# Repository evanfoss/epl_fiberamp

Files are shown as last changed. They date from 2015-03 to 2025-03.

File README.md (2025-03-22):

# EPL FiberAmp

## Description

This device was used with an optical sensor to measure sound pressure levels in space constrained environments. The That end was the sensor the other end of the fiberoptic line was attached to a splitter connecting to two more lines that went to the output and input of this device. The FiberAmp supplies a low noise light source to illuminate down the fiber and a photodiode with matching high gain transimpedance amplifier with AC and DC coupled outputs. The AC coupled output was for making measurements of the sound. The DC output was used for verifying the delicate gold coating was not damaged and that light is still reflecting off of it.

Note: Those of you more aware of physics might want to skip to the section at the end titled "Future".

## Development

Most frequently along the auditory path of cadaver ears. The sensor was a fiberoptic line with a thin gold coating deposited onto it's end viaan evaporation process. The original concept was proved by Lisa Olsen's team earlier. The electronics for this were however started with a clean sheet by Evan Foss and the DC filter network from the earlier EPL revision by Ishmael S. W. The reasoning was simple, the original design and a revised update from EPL earlier were very old and both had seen numerous itterations that added amplifier stages haphazardly. There was also the issue of stability. The earlier EPL update was about 15 years old at least and it was known for periodically becoming unstable and self oscillating for unknown reasons.

### Alternate Versions and Experiments

Part way into the process the project was canceled, later it was uncanceled. This happened a few times. Along the way other features were requested and canceled.

|Feature or Concept         | Designed                  | Tested                | Observations
|:---------------           |:---------------           |:---------------       |:---------------
|Infrasound Measurement     | Yes                       | No                    | The 1/f noise etc of the amplifiers made this notion crazy once more there was serious doubt from the team making the sensors that they were responding at that scale
|Reverse Bias on photodiode | Yes                       | Yes                   | This had no obvious effect on THD+N and was abandoned
|Alternatives for 1st stage opamp| Yes                  | No                    | I had drawn up early versions with a few alternative opamps for that first stage because it was unclear on paper which would perform better

## Toolchain

The development toolchain was as follows:

|Tool Name                                                                                   | License           | Function
|:---------------                                                                            | :-------------    | :-----------------
|<a href="https://www.sagemath.org//">SageMath</a>                                           | Open Source       | Online Mathematics Software
|<a href="https://github.com/lepton-eda/lepton-eda">lepton-eda</a>                           | Open Source       | EDA (Electronic Design Automation) suite lepton-eda a fork of gEDA
|<a href="https://ngspice.sourceforge.io/">ng-spice</a>                                      | Open Source       | Circuit Simulator
|<a href="http://repo.hu/projects/pcb-rnd/">pcb-rnd</a>                                      | Open Source       | CAD (Computer Aided Design) tool for PCB (Printed Circuit Board) layout gEDA/PCB
|<a href="https://gerbv.github.io/">gerbv</a>                                                | Open Source       | Gerber viewer
|<a href="https://www.gnu.org/software/make/">GNU/Make</a>                                   | Open Source       | Toolchain automation
|<a href="https://www.frontpanelexpress.com/front-panel-designer">Front Panel Designer</a>   | Free as in Beer   | Front Panels Express Software

Sadly all my SageMath entries for this project appear lost. I believe a SageMath server refresh some years ago took them out.

The PCB layout was originally done in gEDA/PCB which I believe is defunct. Thankfully pcb-rnd which forked from that project is still fully backward compatible to it.

A partial simulation of the device was created to see how the integrators would behave. It is in the "simulation" directory. I had intended I think to add more to simulate the reverse bias and other ideas but there is so much about the sensor that would need to be characterized for that. All that measurement would basically be just as time consuming and expensive as building a few versions and testing them which was contentious with this projects PI.

## Circuit Design

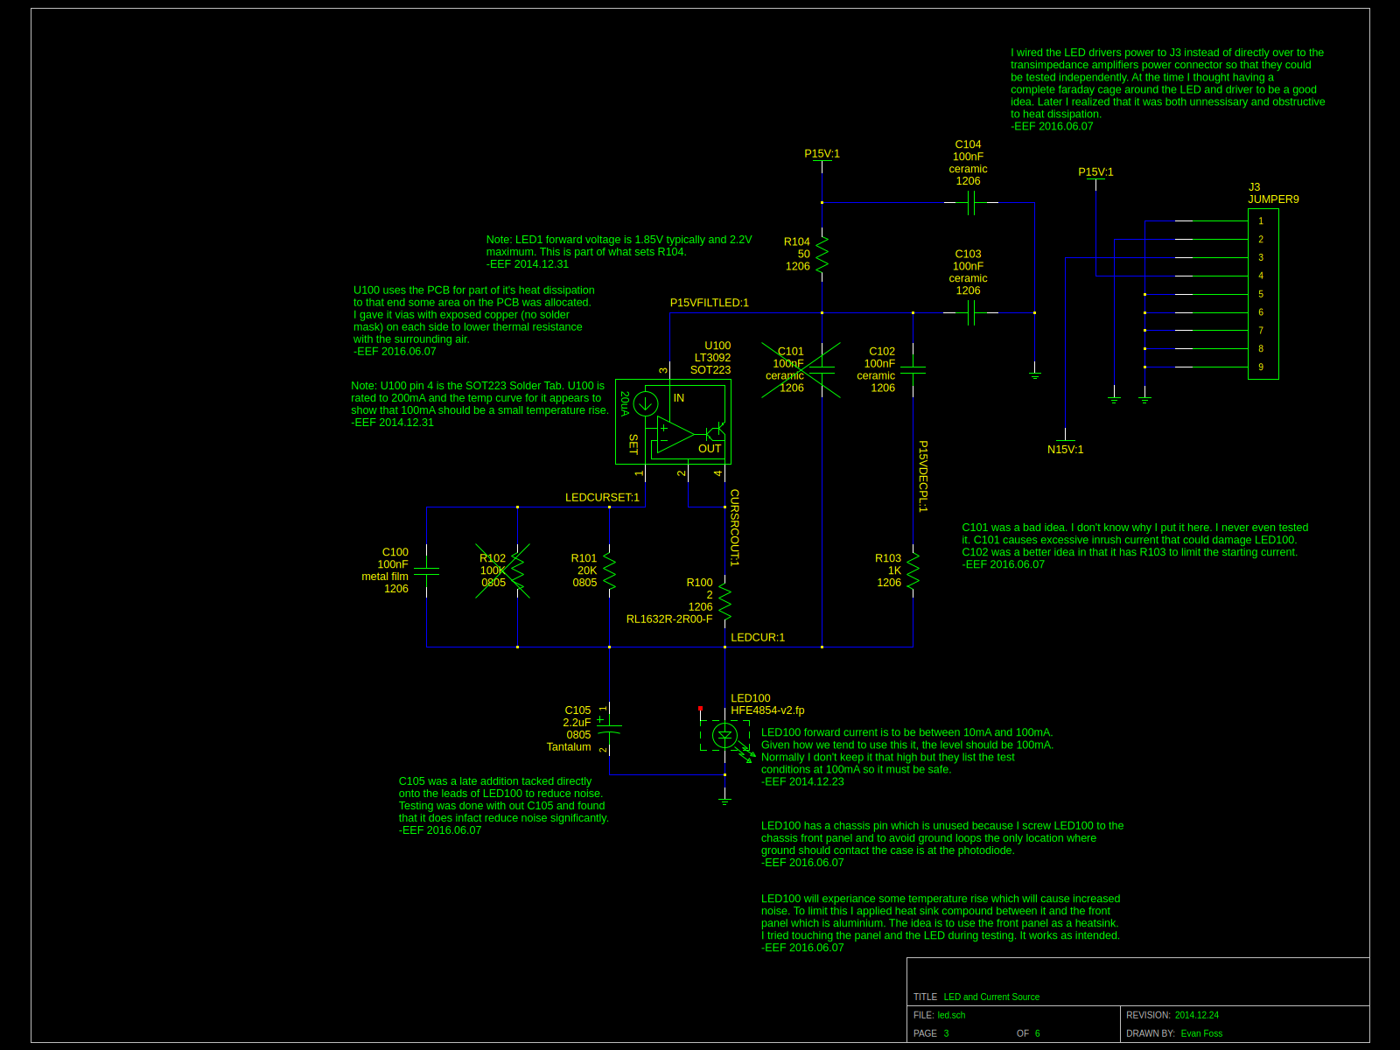
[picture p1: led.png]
|
|:-----------------
|Sch1: led.sch

Sch1 shows the light source for the project. LED100 is the lightsource. The U100 is a constant current source. R104 and C103 attenuate ripples in the power supply and it lowers the amount of power dissipated in U100 and it limits the initial current through C105. R100 is a current shunt. R101 sets the current and C100 reduces the noise R101 contributes. Likewise C105 reduces noise and limits power on current through LED100. 

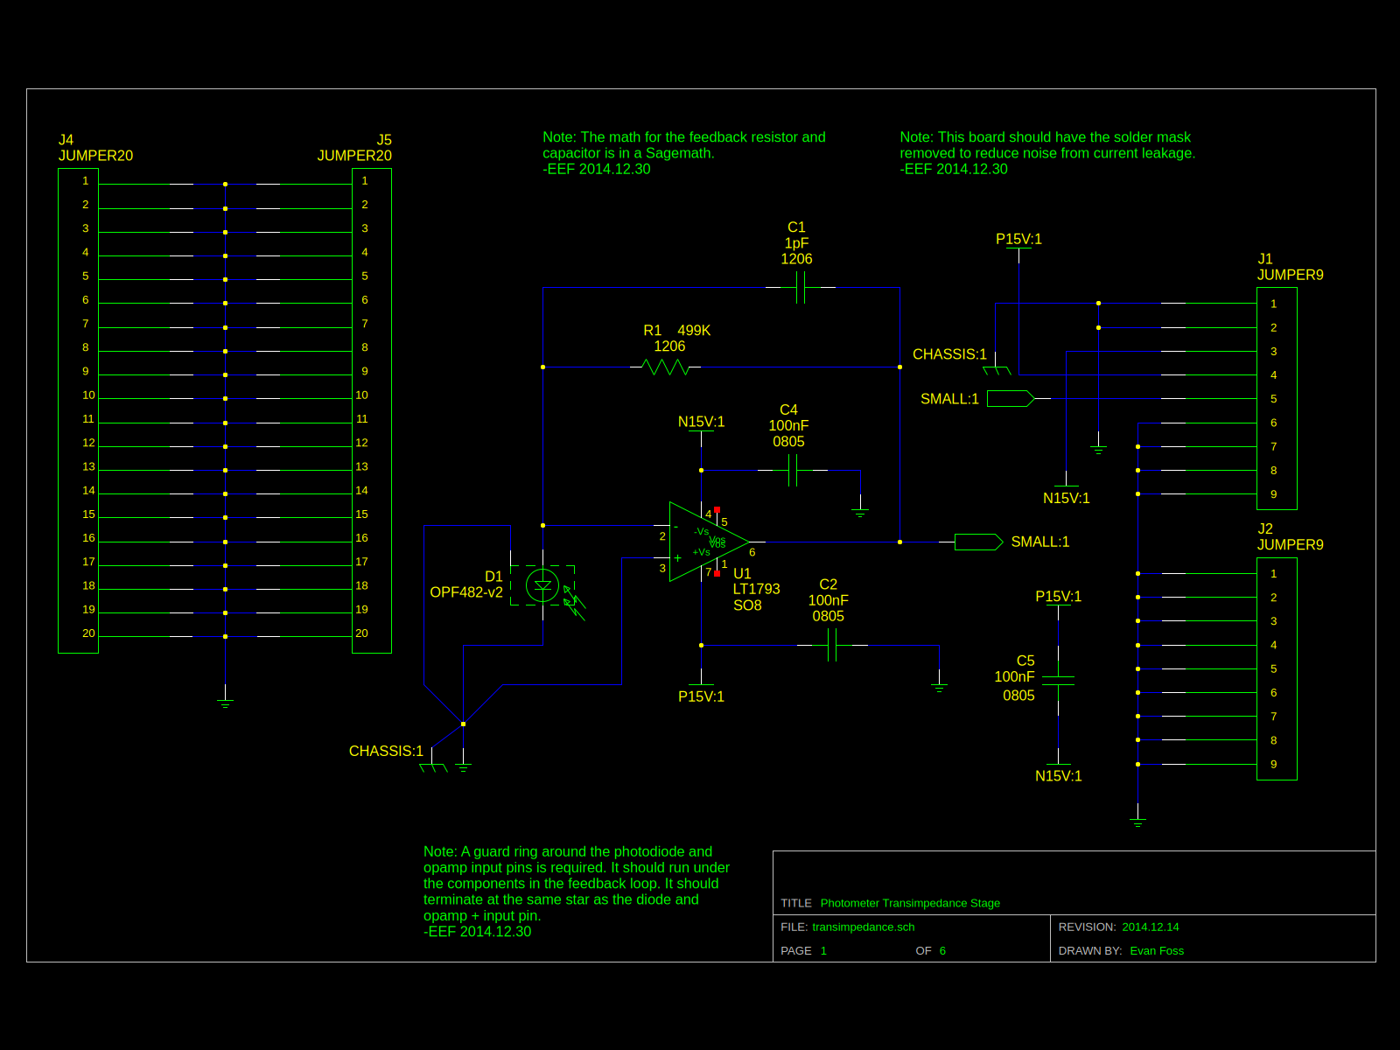
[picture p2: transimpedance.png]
|
|:-----------------
|Sch2: transimpedance.sch

Sch2 was based on the previous work I did for the <a href="https://github.com/evanfoss/epl_photometer">EPL Photometer</a>. The operation is basically the same. Light comes in and is converted to a current by D1. That current goes into a transimpedance amplifier built out of U1. R1 sets the conversion factor from current to voltage. C1 limits the frequency response and the value is tuned per unit for optimate performance. That said at this high of a current ratio it's value is going to be extrodinarily small.

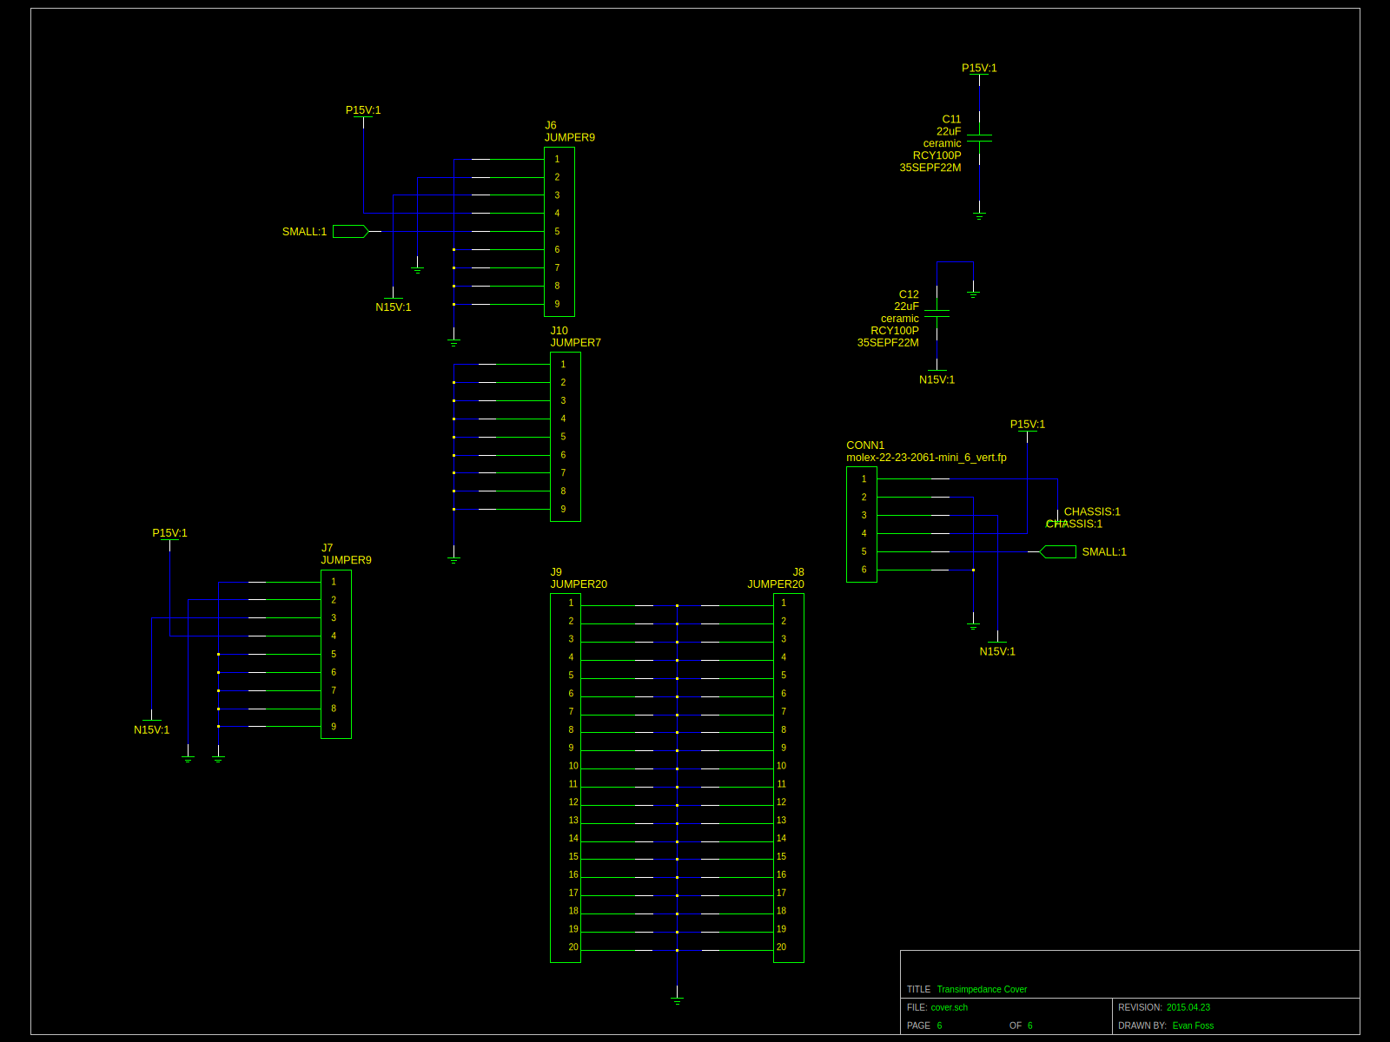
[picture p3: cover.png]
|
|:-----------------
|Sch3: cover.sch

Because Sch1 and Sch2 are in a small subassembly that is off on a cable the back cover (Sch3) has some capacitors for power supply decoupling. The back cover is also there for a very important reason, transimpedance amplifiers are very sensitive to noise. Their input impedance and the output impedance of the photodiode are very low. So the whole assembly has a metal shield around it made with this cover.

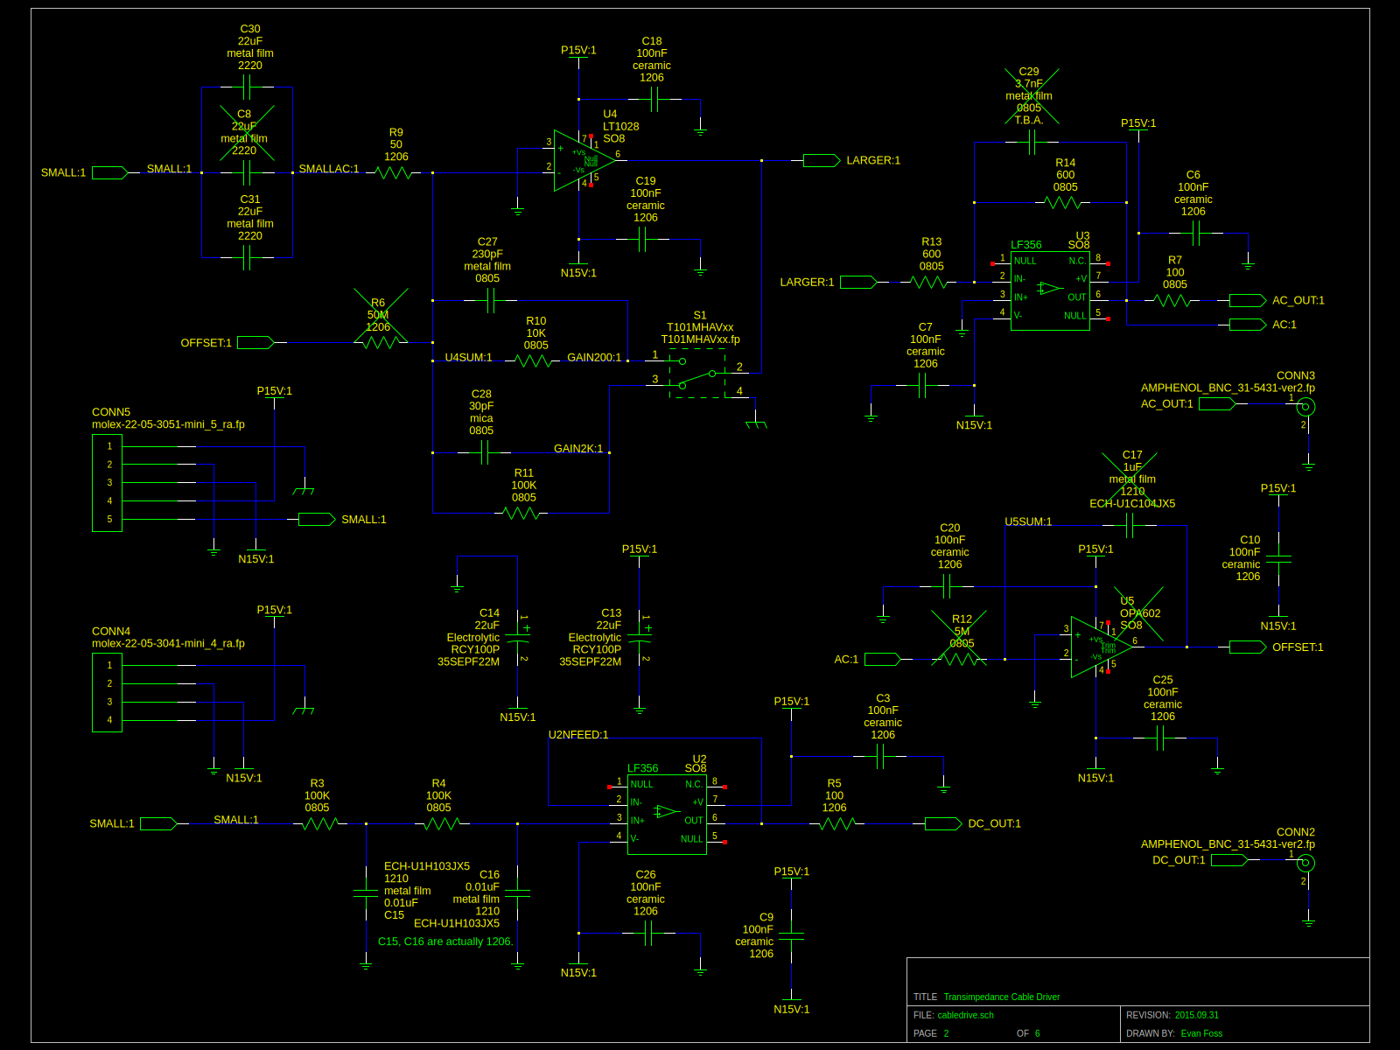
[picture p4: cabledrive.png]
|
|:-----------------
|Sch4: cabledrive.sch

Sch4 has a lot going on. The signal comes in as "SMALL" and is AC Coupled into a gain stage built around U4 with two settings (gain 200/gain 2K) set by S1. The output of this stage goes to two more stages.

The two following stages on the AC coupled path are a cable driver that operates at unity gain made of U3. (This was later changed to add another gain of 10.) The other stage this goes to is an optional integrator for providing an offset to feed back into U4. Earlier versions of this device also used this integrator's output for the DC coupled output. I liked this as it enabled much lower frequency response.

The DC coupled output is built around the RC filter network made of R3, R4, C15, C16. This RC filter was a carry forward from Ishmael's earlier revision of the device. The output of the filter is made stable for driving the cables out of the chamber by U2 which is another amplifier set for unity gain.

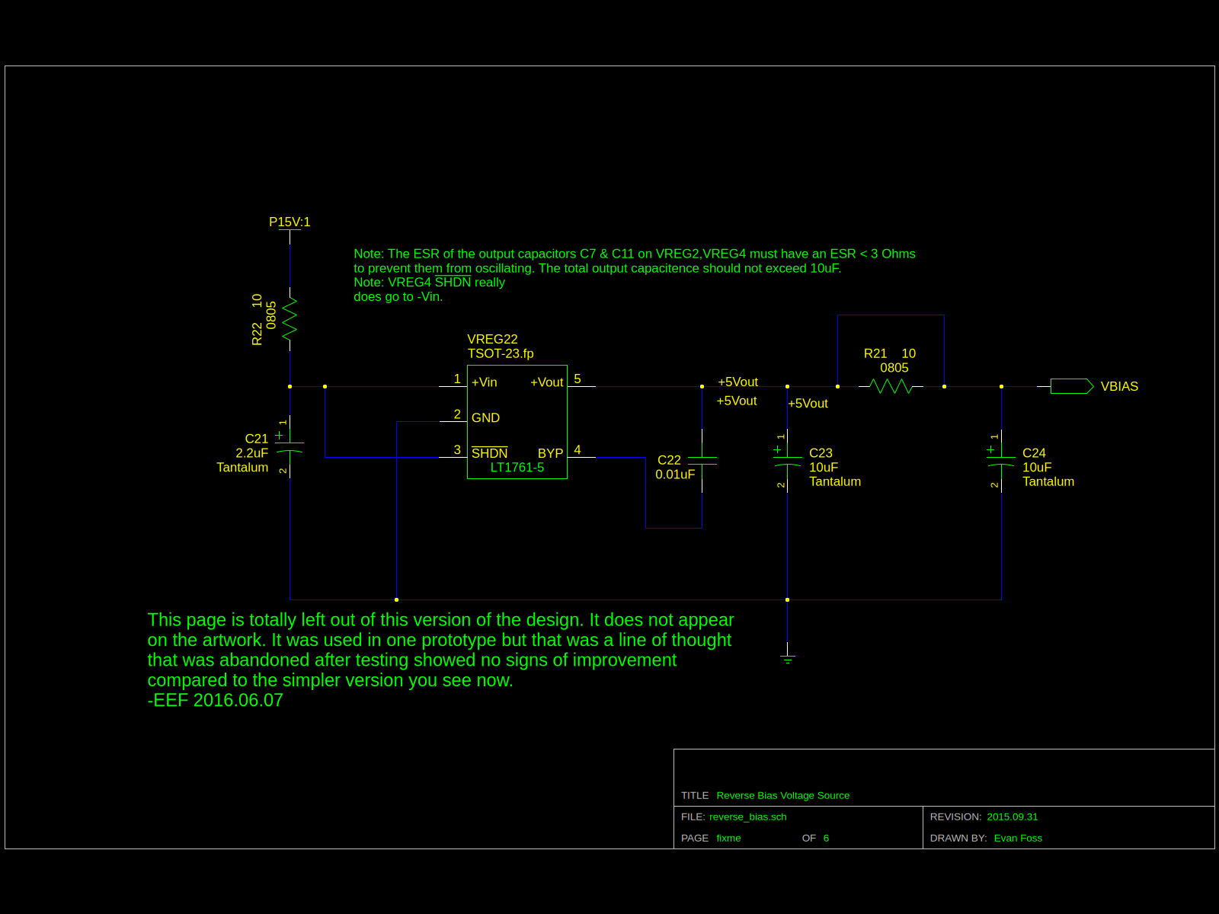
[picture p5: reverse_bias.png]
|
|:-----------------
|Sch5: reverse_bias.sch

Sch5 was something that didn't make the cut into the final device. It was used to provide a voltage source to apply to the bottom of D1 in Sch1. I am including it here so that if someone wants to know how this was built and tested they can see. VREG22 was selected for it's low noise in the frequencies we are concerned with.

### Grounding

Going back to Sch1 there is something worth paying attention too at the botton of D1. The chassis of D1 and the analog common are interconnected. The chassis of D1 had to be at analog common to prevent chassis ground from injecting noise into the transimpedance amplifier but we couldn't have users touching something at analog common that wasn't also tied to proper chassis ground so they had to be connected here. If I had it to do over again this would probably be the same low impedance bridge described in the <a href="https://github.com/evanfoss/eef_bioamp">EEF_BioAmp</a> that originated in the <a href="https://github.com/EPL-Engineering/epl_bioamp">EPL BioAmp</a> it was forked from.

## PCB Layouts

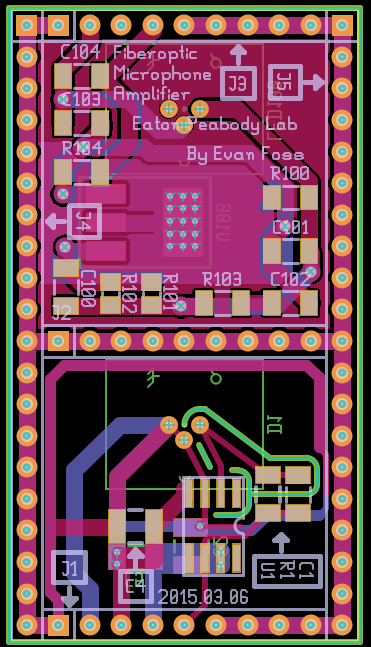
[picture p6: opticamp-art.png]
|
|:-----------------
|PCB1: This is an rendering from the gerber viewer of the opticamp-art pcb. Note the PCB heatsink and routes meant to isolate the most sensitive route near the transimpedance amplifier.

This gerber view doesn't show it but I put a lot of effort into manually hacking the pcb file so that the gerber output would clear the mask around the photodiode and transimpedance amplifier. This has since been fixed with subsiquent software revisions.

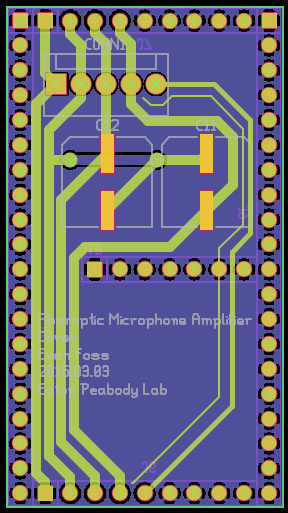
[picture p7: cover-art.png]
|
|:-----------------
|PCB2: This is a rendering from the gerber viewer of the back cover.

This is pretty tame stuff. It's just the larger decoupling capacitors and a sheet of copper to act like a faraday cage over the board it mates too.

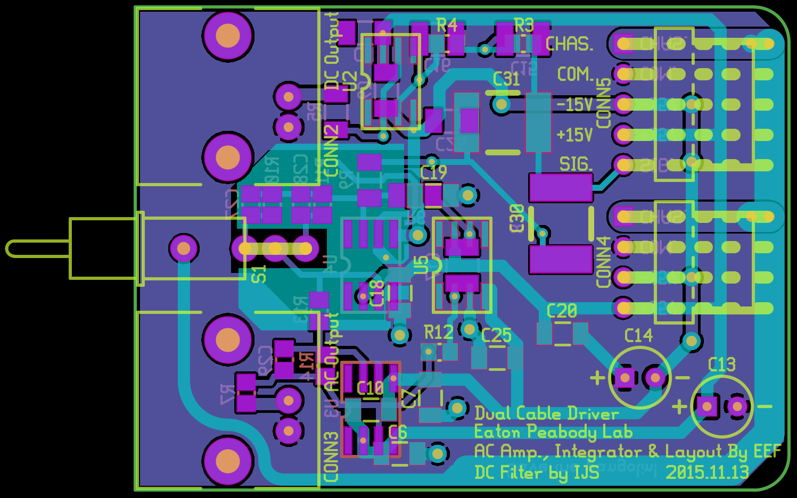
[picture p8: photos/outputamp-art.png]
|
|:-----------------
|PCB3: This is a render from the gerber viewer of the output amplifier PCB.

I hope it is understood when I made the 1st version I didn't know the gain selection switch was going to be required and without funds to redo the front panel I was stuck making this layout kind of convoluted in a way I didn't like.

## Packaging and Construction

The device was designed to fit in the standard subrack enclosure with the following front panel. The limited space on the front panel meant there was no room for an on/off switch unfortunately. 

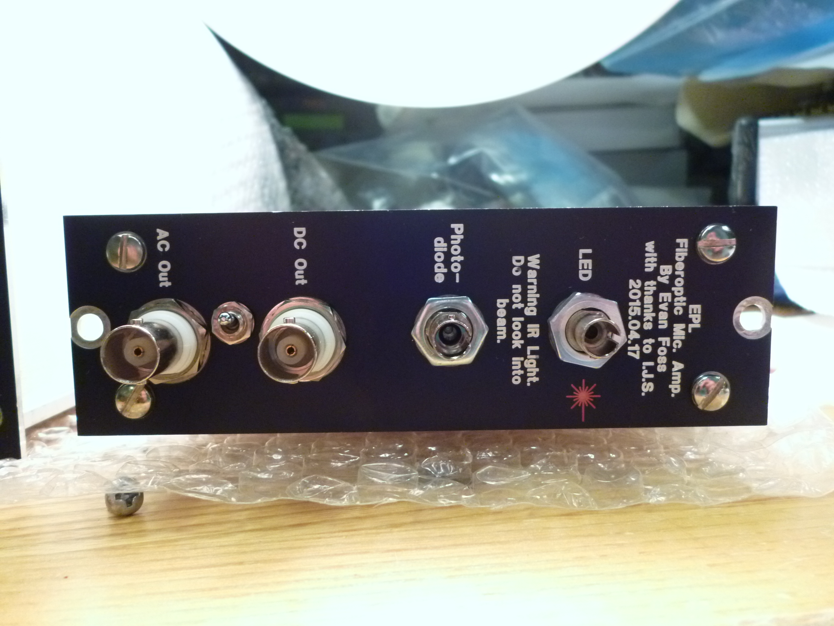
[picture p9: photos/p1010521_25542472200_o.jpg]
|
|:-----------------
|Pic1: Image of the front of the completed device sitting on it's side.

Pic1 shows one of the completed units front panel. The switch for more/less gain was requested by users later in the design and I was not allowed to redo the front panel so dymo labels were applied later.

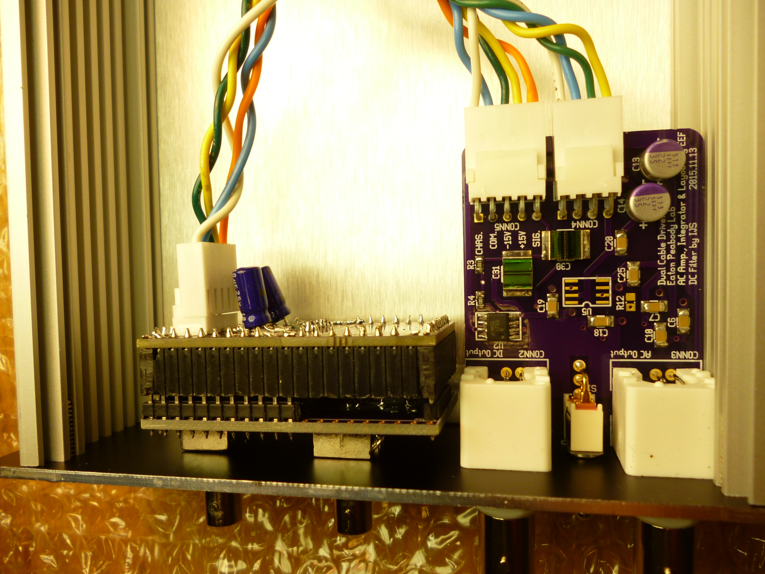
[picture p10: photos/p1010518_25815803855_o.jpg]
|
|:-----------------
|Pic2: Image of the 3 PCBA inside the device facing the top side of the cable driver board.

The problem of aligning everything in the chassis to the front panel and PCBAs was complicated.

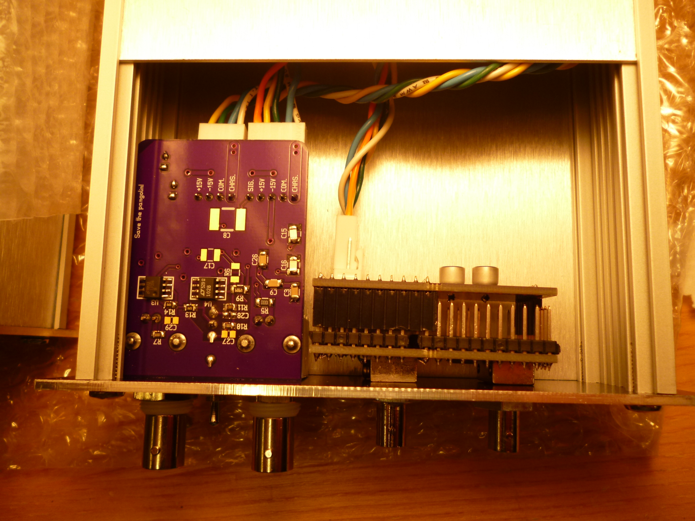
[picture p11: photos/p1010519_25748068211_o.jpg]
|
|:-----------------
|Pic3: Image of the 3 PCBA inside the device facing the bottom side of the cable driver board.

The connectors used to build the faraday cage on the opticamp and back cover so that they were have a gap even when fully mated so tooling could be used to carefully and evenly wedge it open if needed.

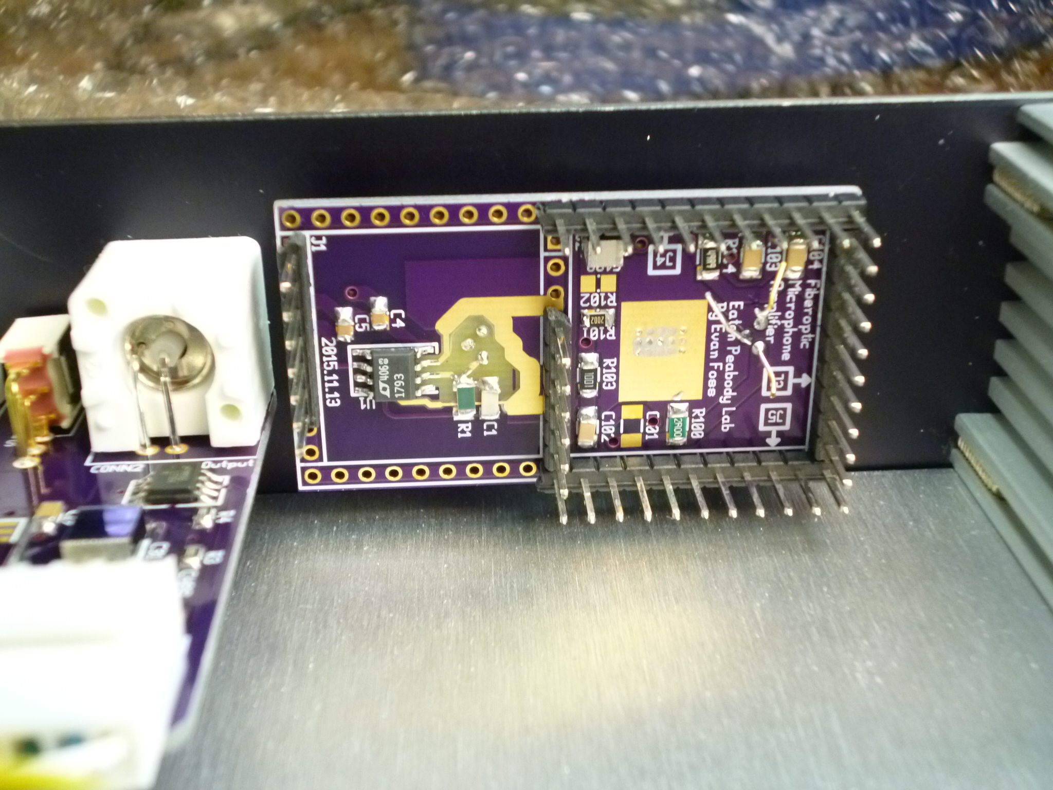
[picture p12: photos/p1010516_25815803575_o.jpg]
|
|:-----------------
|Pic4: Image of the back of the opticamp-art board. The front just has the photodiode and LED on it in their ST mount packages. Note the leads on the LED were left long for testing and trimmed later.

It's worth pointing out that the soldering must be done with washable flux solder. The PCB was washed carefully with the sensors capped. There are rubber caps used on the LED's during shipping and two of those were applied during the cleaning process.

This is how the TIA (TransImpedance Amplifier) looks so clean.

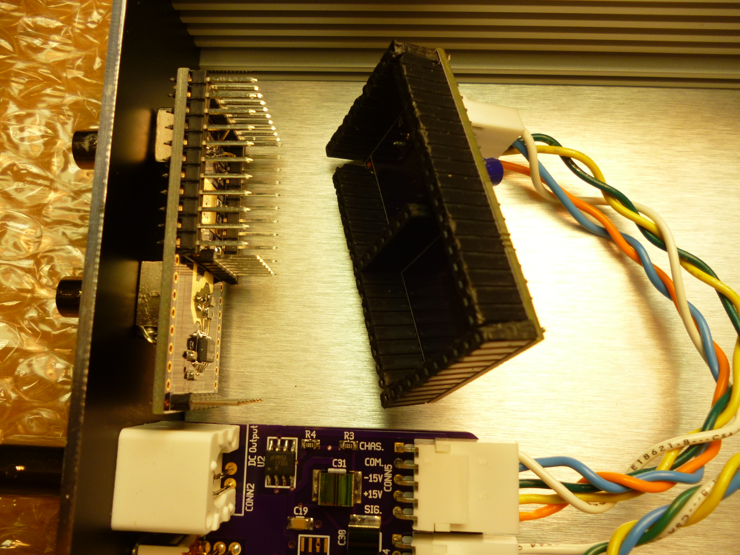
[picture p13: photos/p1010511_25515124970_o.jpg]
|
|:-----------------
|Pic5: Image of the rear cover removed showing how the connectors on the side form a shield.

I just wanted to show that it does detach for completeness.

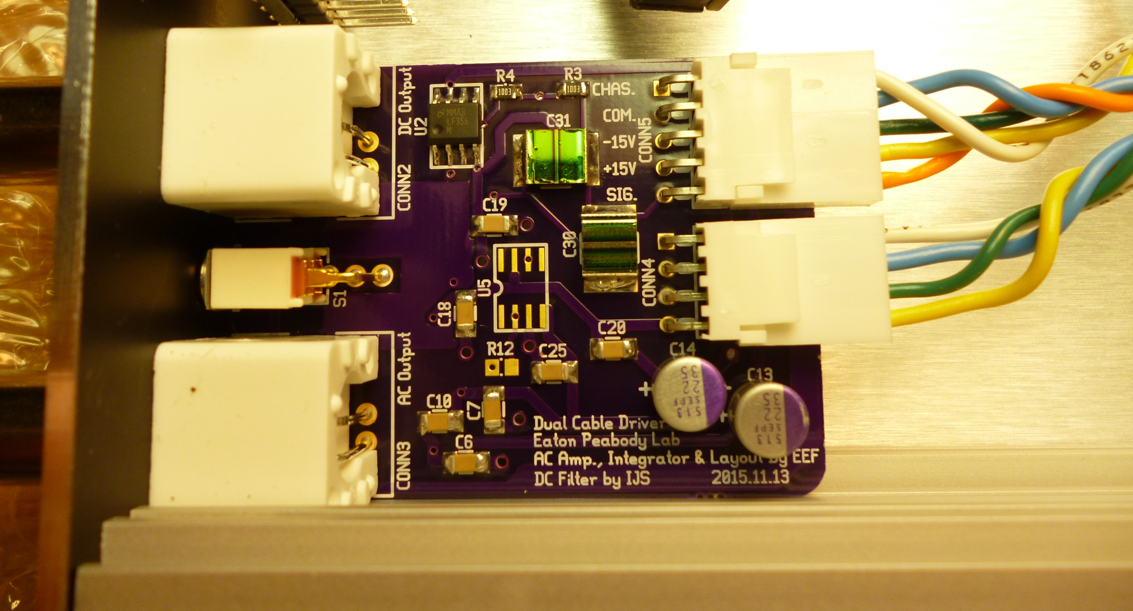
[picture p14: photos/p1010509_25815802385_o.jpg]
|
|:-----------------
|Pic6: Image of the top of the cable driver board.

The output amp board also was build using washable flux solder.

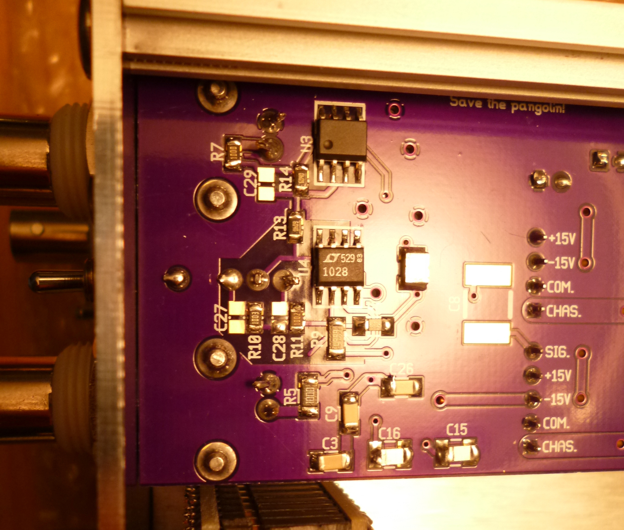
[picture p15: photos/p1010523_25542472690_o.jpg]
|
|:-----------------
|Pic7: Image of the bottom of assembled cable driver board.

I wish I had a better photo of this. C27, C28, and C29 were tuned after the photo. They were left open by request of the PI initially.

## Testing

Mike Ravicz did the testing in the chamber as the sensor was needed. The testing of an earlier "simple" version remains in the project in the "testing" directory. Some attempts at noise floor measurement were made in the simplest terms looking at "dark" current noise out of the sensor using a cover on the photodiode and an HP403B RMS Volt Meter. The problem is even when the device is not "detecting" anything the photodiode is not in darkness. So a loop back fiber with a large attenuator might have made sense but it was not available. The final version was deamed to be an improvement and was put into some use.

## Future

### A word about physics

At the time the device was designed it was assumed by everyone that the operating principle was this:
Light shines down the fiber, bounces off the coating, and sound pushing on the coating causes AM modulation of the returning light.

The more I worked on the fiberamp the more apparent it became that this was not the case. The actual effect happening is a laser dopplar vibrometer. Meaning the device was not AM modulating at all but the self interferance of the light coming back off the coating was creating the effect. This explains why the earlier designs worked as well as they did, the added stages with haphazard gains caused distortion that was unintentionally making a demodulating effect.

This also explains why a large number of the optical assemblies made were never working. The length of the fiberoptic cables has to be matched to within fractions of a wavelength. The team was attributing this to issues in the coating process and had spent years refining that process not realizing the coating was likely fine. I believe this modulated waveform might also be the source of the "self oscillation" that the users were seeing in the earlier EPL revision of the device.

All future work on this device should really be around:
1. Changing to a single light source with integrated photodiode so the optical splitter is removed
2. Altering the optics to just be a coated fiber without the added splitter and it's two cables
3. Retailoring the transimpedance source to the bandwidth required for an LDV frontend
4. Using a more cohearant source of light
5. Adopting the grounding plan I introduced in the BioAmp where the devices in the subrack only use an RC bridge between analog common and chassis instead of the short between them currently in use.
6. An on/off switch so the user can swap sensors without turning the subrack power on and off.

Of these goals I believe 1, 2, 3, 5, and 6 are easily possible with minor modifications but 4 might be an issue. The problem I have is that a lot of fiber coupled LED/Photodiode pairs I find are not clear on if the part is using a laser diode or just an LED. I suspect many of the LEDs are actually "cohearent enough" for our purposes.

All this said after I left EPL it is my understanding that they switched to a commercially made device. So all this is just being documented for future refrence.

### A minor note about tools

The PCB layout for the device required a number of features including removing soldermask from around some traces that was at the time not a feature of the PCB design software (gEDA/PCB now defunct). This and other features are now standard in PCB-RND and much easier to use. So migration there would be an advantage.

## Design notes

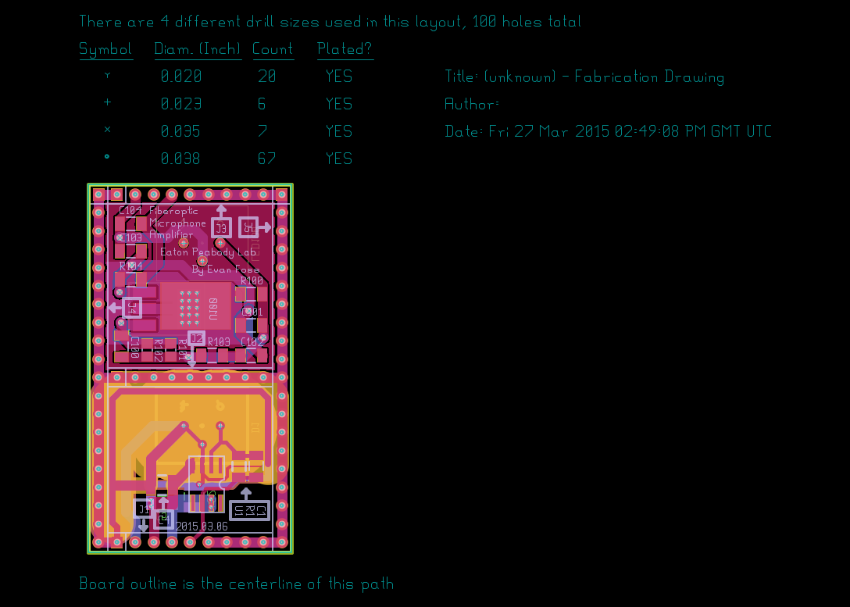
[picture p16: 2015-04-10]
mask cleared/opticamp-art.png

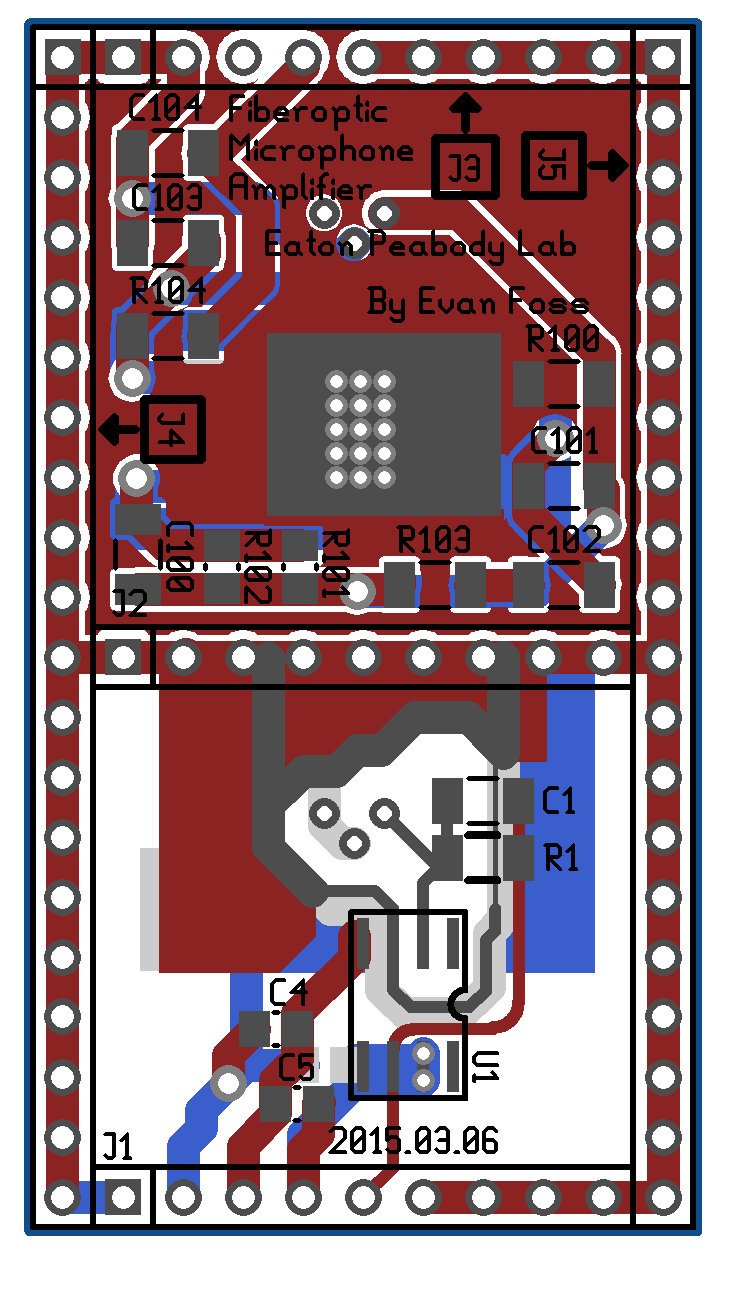
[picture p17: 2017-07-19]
oshpark/opticamp_woroute/opticamp-art.png

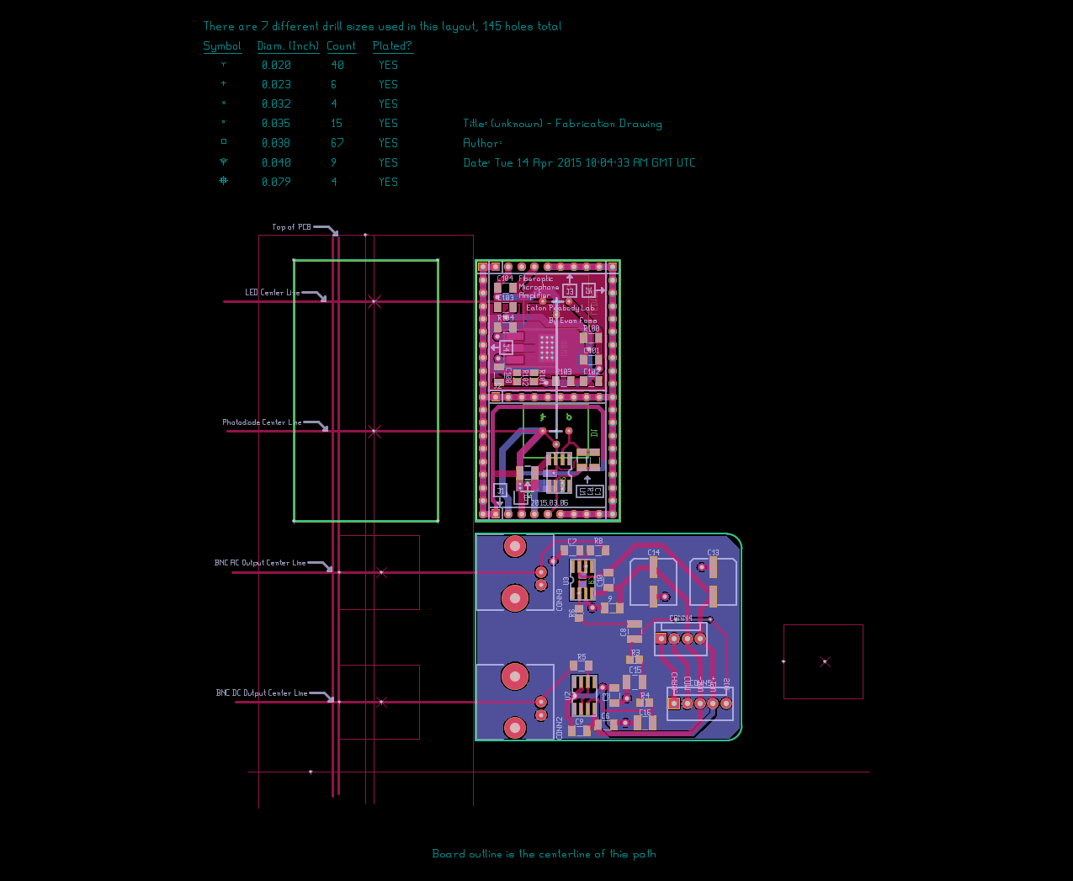
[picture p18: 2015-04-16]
front panel/opticamp-art.png

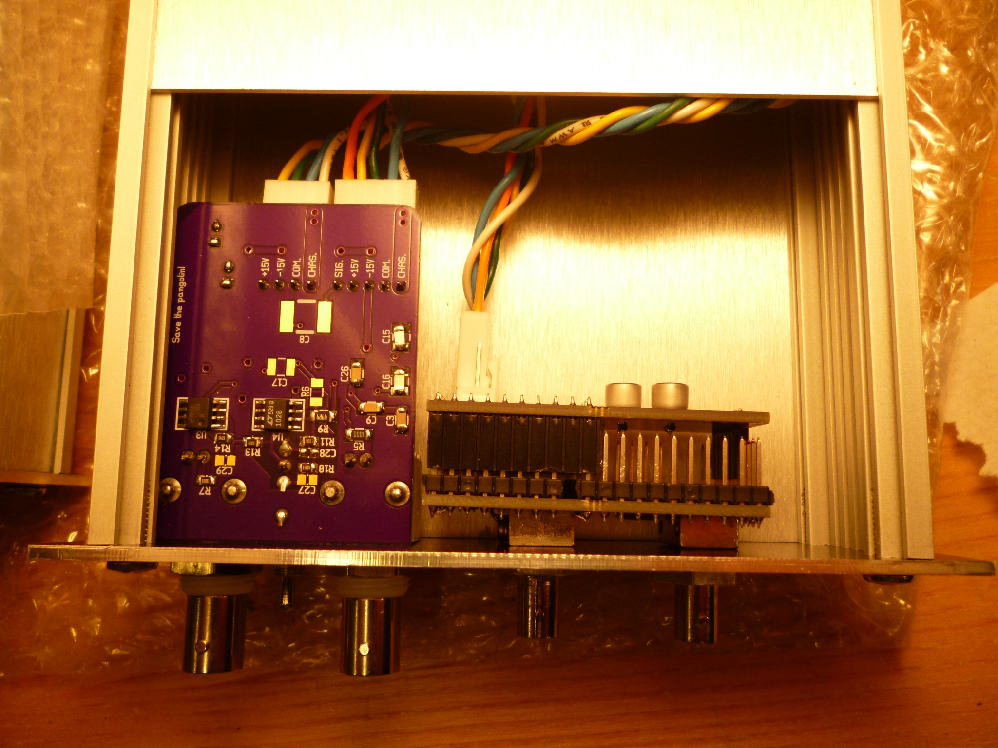
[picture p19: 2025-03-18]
photos/p1010520_25817118386_o.jpg

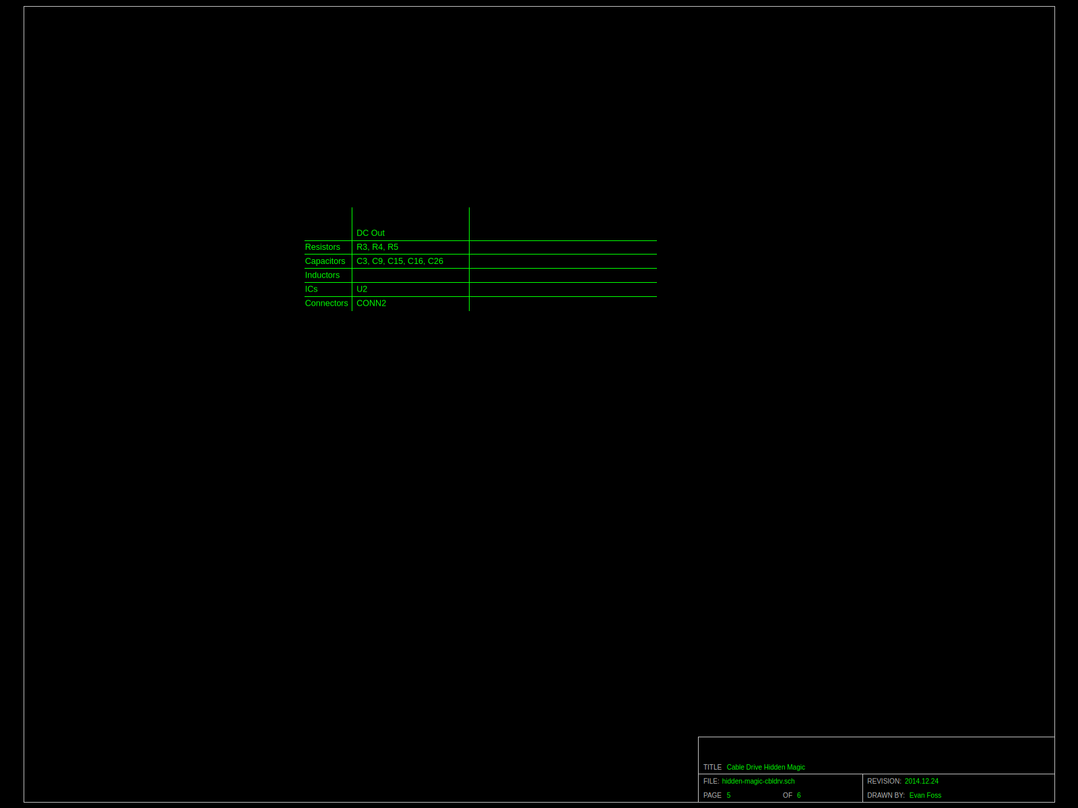
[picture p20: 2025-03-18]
hidden-magic-cbldrv.png

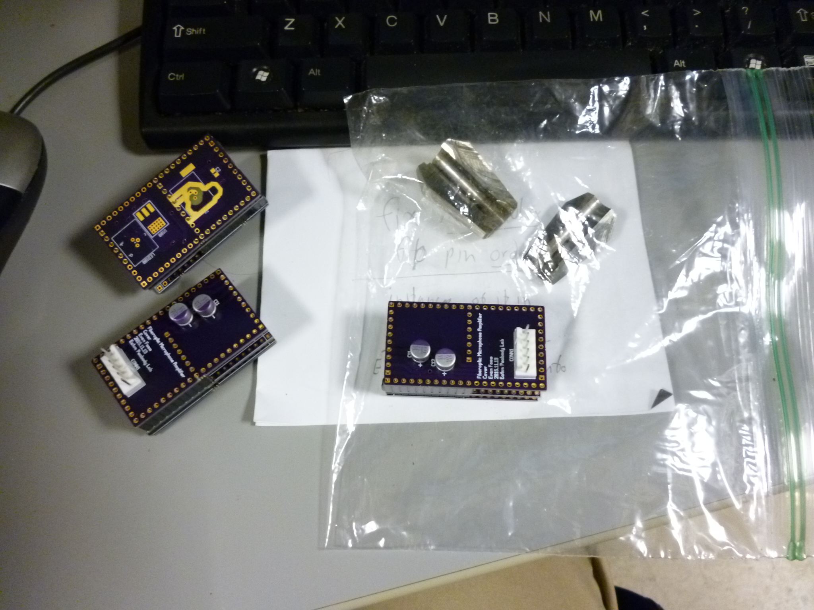
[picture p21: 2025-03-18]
photos/p1010492_25720703111_o.jpg

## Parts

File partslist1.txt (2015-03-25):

.START
..refdes	device	value	footprint	quantity
C1	CAPACITOR	2.7pF	1206	1
C10	CAPACITOR	100nF	1206	1
C100	CAPACITOR	100nF	1206	1
C101	CAPACITOR	100nF	1206	1
C102	CAPACITOR	100nF	1206	1
C103	CAPACITOR	1uF	1206	1
C104	CAPACITOR	100nF	1206	1
C11	CAPACITOR	10uF	NICHICON_WT_CAP_8_5p4	1
C12	CAPACITOR	10uF	NICHICON_WT_CAP_8_5p4	1
C13	CAPACITOR	10uF	NICHICON_WT_CAP_8_5p4	1
C14	CAPACITOR	10uF	NICHICON_WT_CAP_8_5p4	1
C15	CAPACITOR	2.2uF	1210	1
C16	CAPACITOR	2.2uF	1210	1
C2	CAPACITOR	100nF	1210	1
C3	CAPACITOR	100nF	1206	1
C4	CAPACITOR	100nF	1210	1
C5	CAPACITOR	100nF	1206	1
C6	CAPACITOR	100nF	1206	1
C7	CAPACITOR	100nF	1206	1
C8	CAPACITOR	2.2uF	1210	1
C9	CAPACITOR	100nF	1206	1
CONN1	CONNECTOR_5	unknown	molex-22-23-2051-mini_5_vert.fp	1
CONN2	BNC	unknown	AMPHENOL_BNC_31-5431-ver2.fp	1
CONN3	BNC	unknown	AMPHENOL_BNC_31-5431-ver2.fp	1
CONN4	CONNECTOR_4	unknown	molex-22-23-2041-mini_4_vert.fp	1
CONN5	CONNECTOR_5	unknown	molex-22-23-2051-mini_5_vert.fp	1
D1	photodiode	TEMD6xxx	OPF482	1
J1	CONNECTOR_9	unknown	JUMPER9	1
J10	CONNECTOR_9	unknown	JUMPER7	1
J2	CONNECTOR_9	unknown	JUMPER9	1
J3	CONNECTOR_9	unknown	JUMPER9	1
J4	CONNECTOR_20	unknown	JUMPER20	1
J5	CONNECTOR_20	unknown	JUMPER20	1
J6	CONNECTOR_9	unknown	JUMPER9	1
J7	CONNECTOR_9	unknown	JUMPER9	1
J8	CONNECTOR_20	unknown	JUMPER20	1
J9	CONNECTOR_20	unknown	JUMPER20	1
LED100	photodiode	unknown	HFE4854.fp	1
R1	RESISTOR	1M	1206	1
R100	RESISTOR	2	1206	1
R101	RESISTOR	20K	0805	1
R102	RESISTOR	100K	0805	1
R103	RESISTOR	1K	1206	1
R104	RESISTOR	50	1206	1
R3	RESISTOR	5K	0805	1
R4	RESISTOR	5K	0805	1
R5	RESISTOR	100	1206	1
R6	RESISTOR	1K	0805	1
R7	RESISTOR	6.65K	0805	1
R8	RESISTOR	100	1206	1
U1	OPAMP	LT1793	SO8	1
U100	LT3092	unknown	SOT223	1
U2	LF356	LF356	SO8	1
U3	LF356	LF356	SO8	1
.END

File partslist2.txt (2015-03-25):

.START
..refdes	device	value	footprint	quantity
CONN2	BNC	unknown	AMPHENOL_BNC_31-5431-ver2.fp	1
CONN3	BNC	unknown	AMPHENOL_BNC_31-5431-ver2.fp	1
C10	CAPACITOR	100nF	1206	1
C100	CAPACITOR	100nF	1206	1
C101	CAPACITOR	100nF	1206	1
C102	CAPACITOR	100nF	1206	1
C104	CAPACITOR	100nF	1206	1
C3	CAPACITOR	100nF	1206	1
C5	CAPACITOR	100nF	1206	1
C6	CAPACITOR	100nF	1206	1
C7	CAPACITOR	100nF	1206	1
C9	CAPACITOR	100nF	1206	1
C2	CAPACITOR	100nF	1210	1
C4	CAPACITOR	100nF	1210	1
C11	CAPACITOR	10uF	NICHICON_WT_CAP_8_5p4	1
C12	CAPACITOR	10uF	NICHICON_WT_CAP_8_5p4	1
C13	CAPACITOR	10uF	NICHICON_WT_CAP_8_5p4	1
C14	CAPACITOR	10uF	NICHICON_WT_CAP_8_5p4	1
C103	CAPACITOR	1uF	1206	1
C15	CAPACITOR	2.2uF	1210	1
C16	CAPACITOR	2.2uF	1210	1
C8	CAPACITOR	2.2uF	1210	1
C1	CAPACITOR	2.7pF	1206	1
J4	CONNECTOR_20	unknown	JUMPER20	1
J5	CONNECTOR_20	unknown	JUMPER20	1
J8	CONNECTOR_20	unknown	JUMPER20	1
J9	CONNECTOR_20	unknown	JUMPER20	1
CONN4	CONNECTOR_4	unknown	molex-22-23-2041-mini_4_vert.fp	1
CONN1	CONNECTOR_5	unknown	molex-22-23-2051-mini_5_vert.fp	1
CONN5	CONNECTOR_5	unknown	molex-22-23-2051-mini_5_vert.fp	1
J10	CONNECTOR_9	unknown	JUMPER7	1
J1	CONNECTOR_9	unknown	JUMPER9	1
J2	CONNECTOR_9	unknown	JUMPER9	1
J3	CONNECTOR_9	unknown	JUMPER9	1
J6	CONNECTOR_9	unknown	JUMPER9	1
J7	CONNECTOR_9	unknown	JUMPER9	1
U2	LF356	LF356	SO8	1
U3	LF356	LF356	SO8	1
U100	LT3092	unknown	SOT223	1
U1	OPAMP	LT1793	SO8	1
D1	photodiode	TEMD6xxx	OPF482	1
LED100	photodiode	unknown	HFE4854.fp	1
R5	RESISTOR	100	1206	1
R8	RESISTOR	100	1206	1
R102	RESISTOR	100K	0805	1
R6	RESISTOR	1K	0805	1
R103	RESISTOR	1K	1206	1
R1	RESISTOR	1M	1206	1
R100	RESISTOR	2	1206	1
R101	RESISTOR	20K	0805	1
R104	RESISTOR	50	1206	1
R3	RESISTOR	5K	0805	1
R4	RESISTOR	5K	0805	1
R7	RESISTOR	6.65K	0805	1
.END

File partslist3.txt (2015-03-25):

.START
..device	value	footprint	quantity	refdes
BNC	unknown	AMPHENOL_BNC_31-5431-ver2.fp	2	CONN2 CONN3
CAPACITOR	100nF	1206	10	C10 C100 C101 C102 C104 C3 C5 C6 C7 C9
CAPACITOR	100nF	1210	2	C2 C4
CAPACITOR	10uF	NICHICON_WT_CAP_8_5p4	4	C11 C12 C13 C14
CAPACITOR	1uF	1206	1	C103
CAPACITOR	2.2uF	1210	3	C15 C16 C8
CAPACITOR	2.7pF	1206	1	C1
CONNECTOR_20	unknown	JUMPER20	4	J4 J5 J8 J9
CONNECTOR_4	unknown	molex-22-23-2041-mini_4_vert.fp	1	CONN4
CONNECTOR_5	unknown	molex-22-23-2051-mini_5_vert.fp	2	CONN1 CONN5
CONNECTOR_9	unknown	JUMPER7	1	J10
CONNECTOR_9	unknown	JUMPER9	5	J1 J2 J3 J6 J7
LF356	LF356	SO8	2	U2 U3
LT3092	unknown	SOT223	1	U100
OPAMP	LT1793	SO8	1	U1
photodiode	TEMD6xxx	OPF482	1	D1
photodiode	unknown	HFE4854.fp	1	LED100
RESISTOR	100	1206	2	R5 R8
RESISTOR	100K	0805	1	R102
RESISTOR	1K	0805	1	R6
RESISTOR	1K	1206	1	R103
RESISTOR	1M	1206	1	R1
RESISTOR	2	1206	1	R100
RESISTOR	20K	0805	1	R101
RESISTOR	50	1206	1	R104
RESISTOR	5K	0805	2	R3 R4
RESISTOR	6.65K	0805	1	R7
.END

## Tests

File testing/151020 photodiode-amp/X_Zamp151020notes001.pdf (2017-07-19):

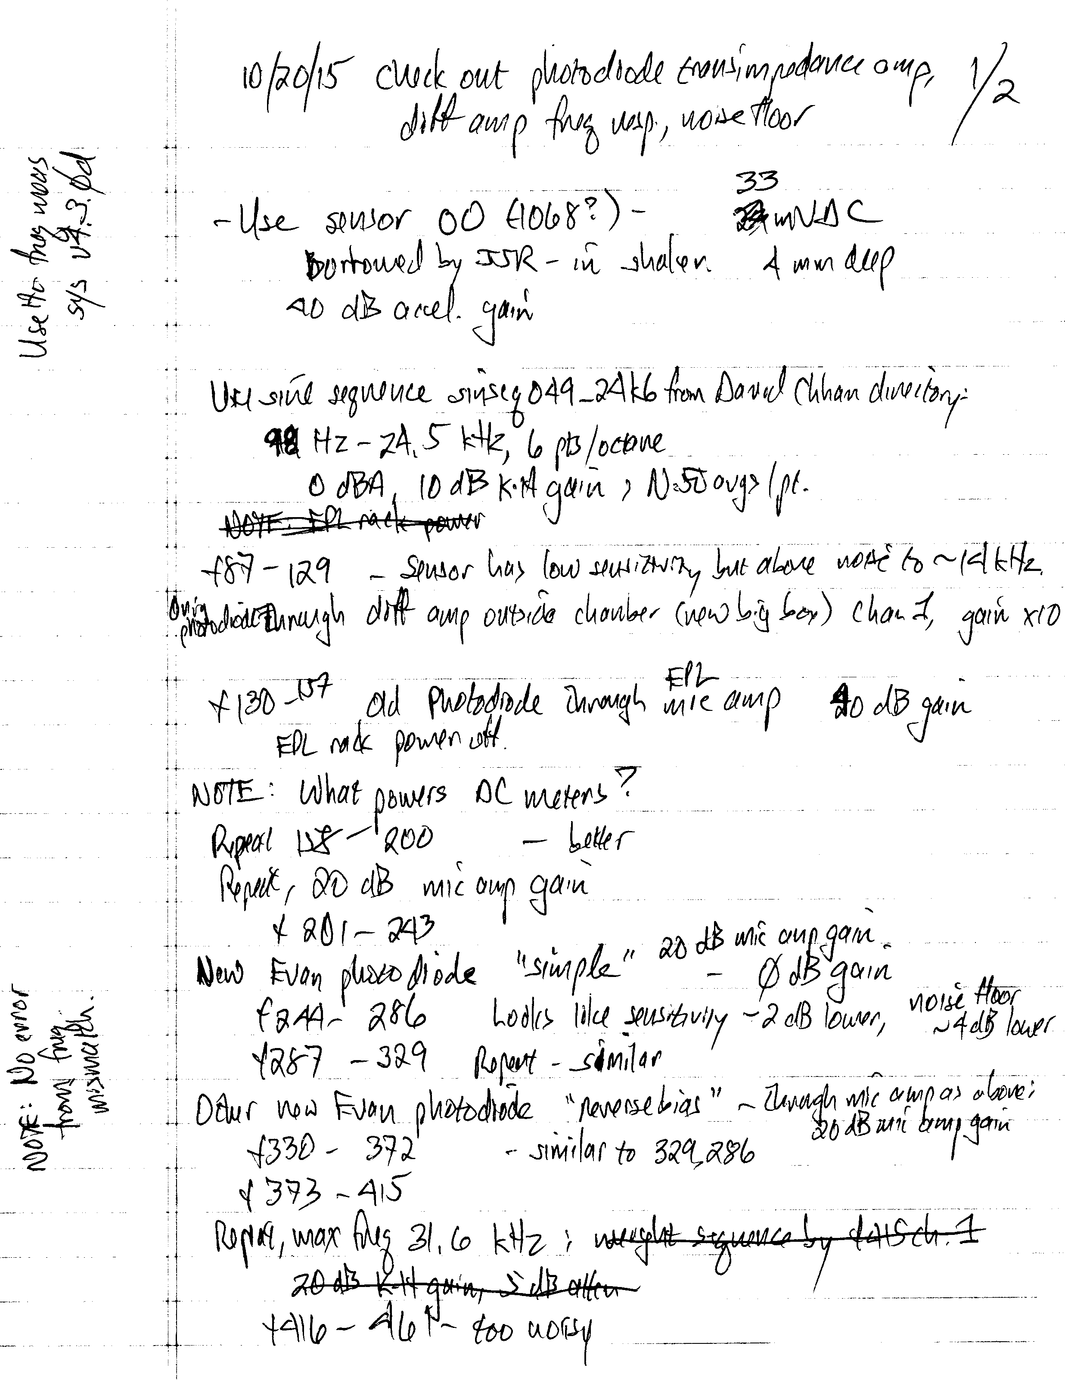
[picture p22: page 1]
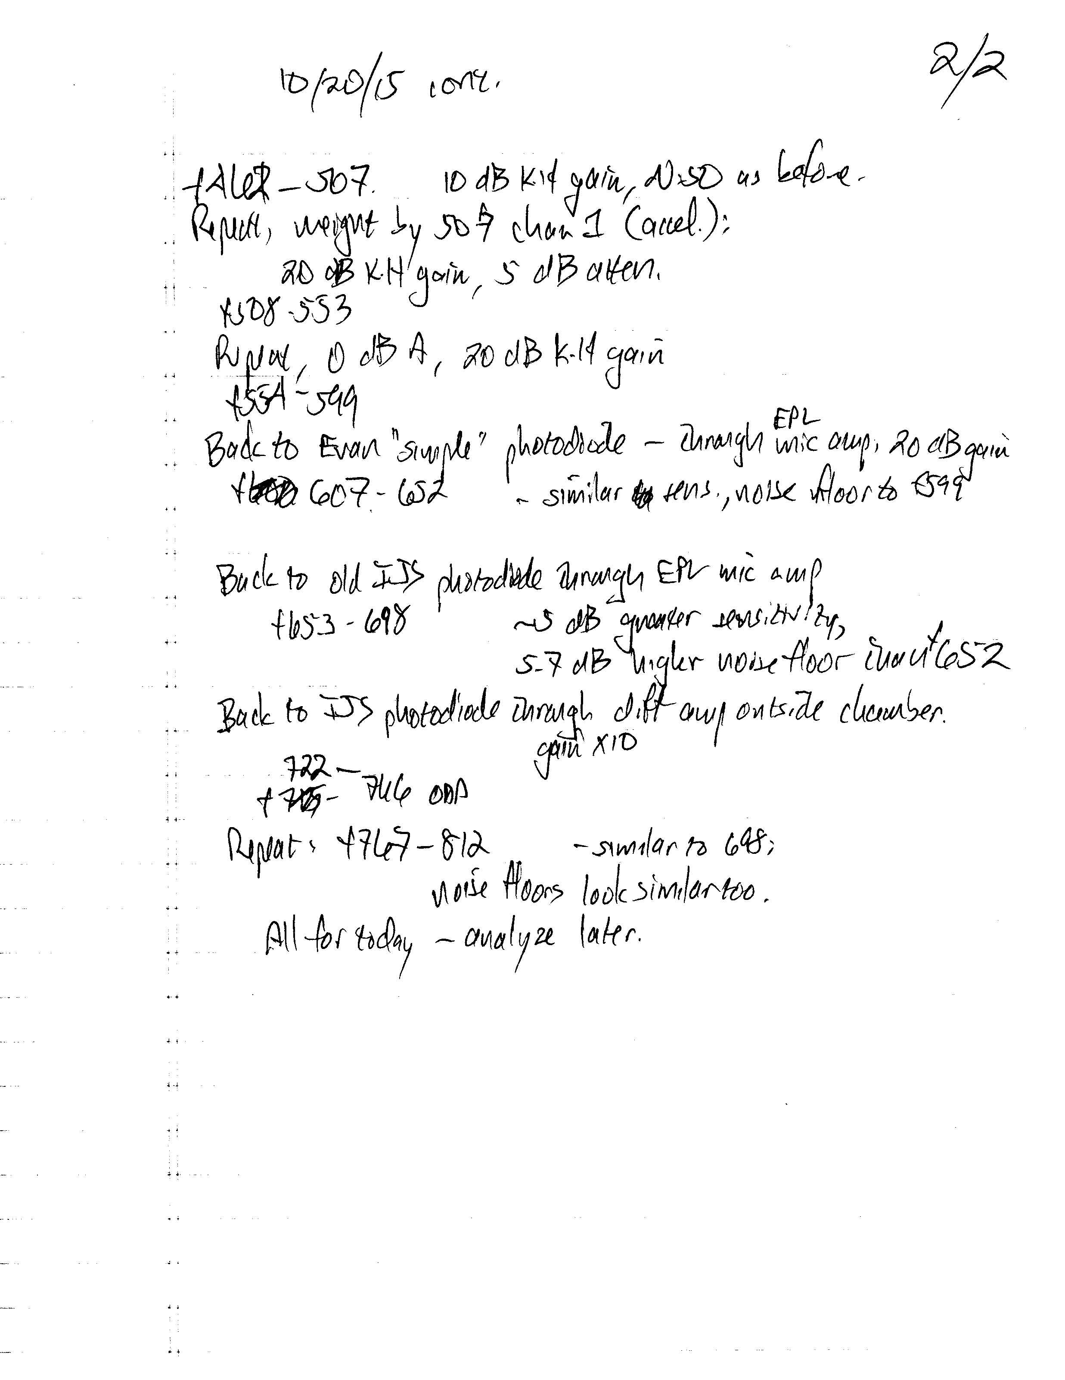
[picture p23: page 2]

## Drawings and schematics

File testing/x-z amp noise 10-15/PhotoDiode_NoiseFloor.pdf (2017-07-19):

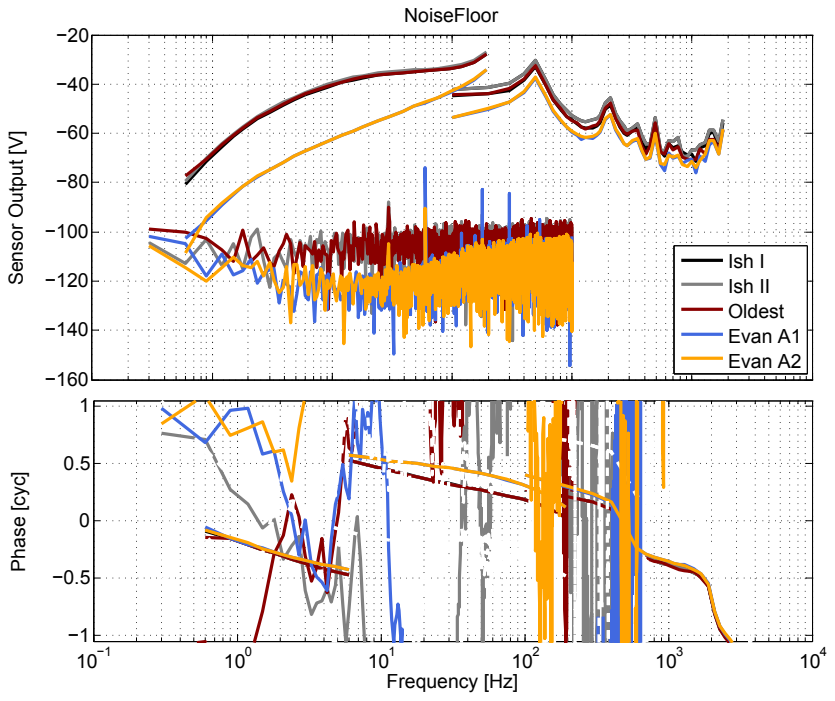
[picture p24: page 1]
Phase [cyc]; Frequency [Hz]; Sensor Output [V]; NoiseFloor

Ish I
Ish II Oldest

Evan A1 Evan A2

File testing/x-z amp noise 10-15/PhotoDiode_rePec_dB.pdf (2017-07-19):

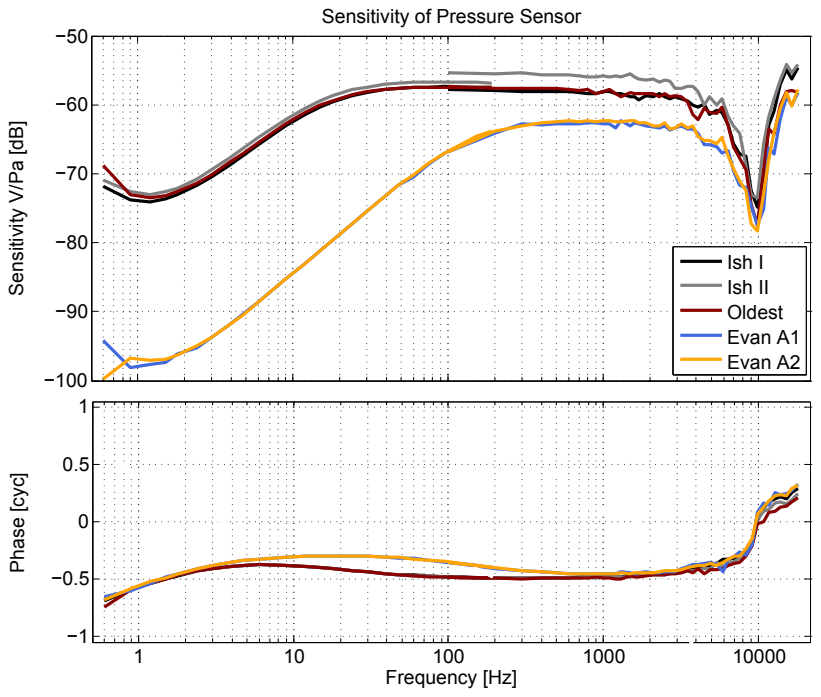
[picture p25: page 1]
Phase [cyc]; Frequency [Hz]; Ish I Ish II Oldest Evan A1 Evan A2

Sensitivity of Pressure Sensor

Sensitivity V/Pa [dB]

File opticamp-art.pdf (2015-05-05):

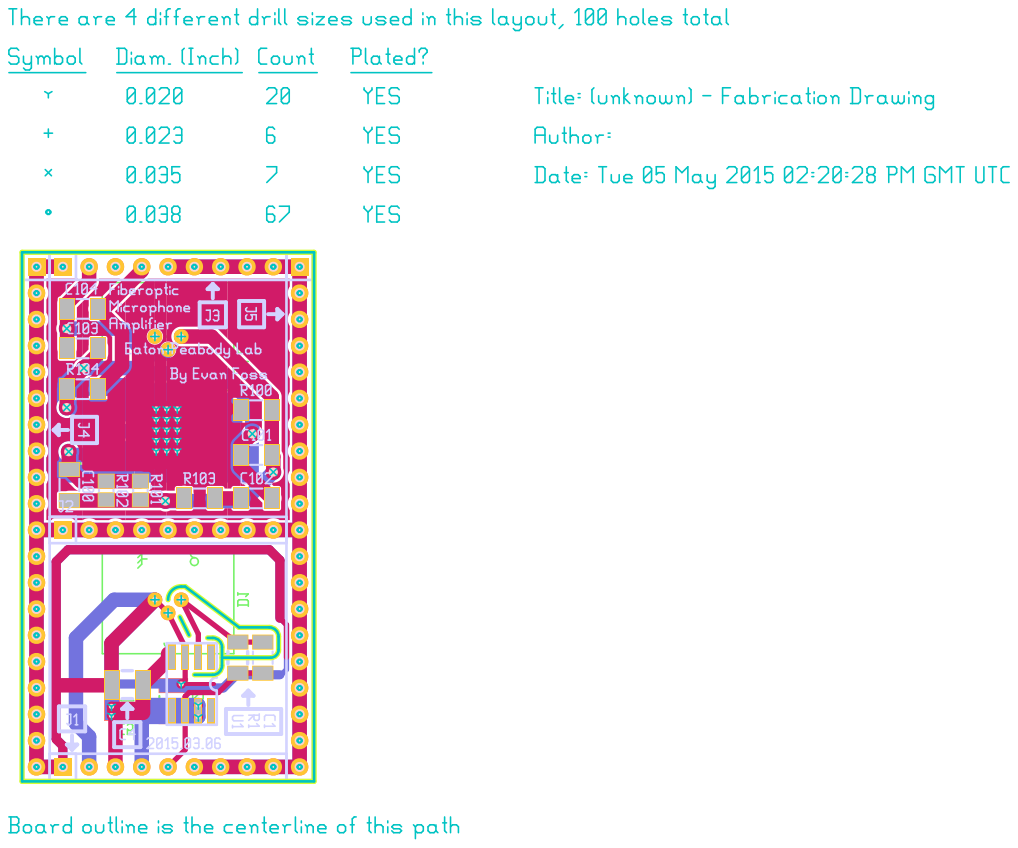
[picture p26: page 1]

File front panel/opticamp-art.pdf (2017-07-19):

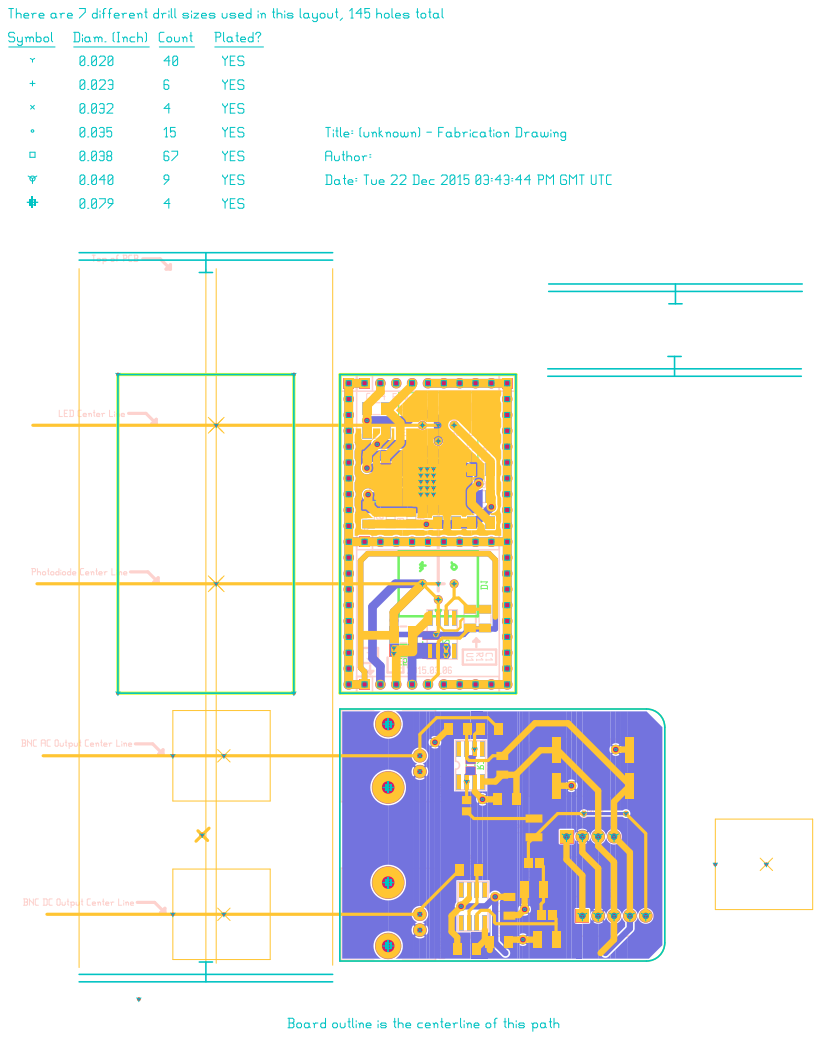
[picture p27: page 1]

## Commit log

2014-10-01 starting to change the architecture of the layout
    [cabledrive.sch, hidden-magic.sch, transimpedance.sch]
2014-10-02 started in on the led and associated current source
    [hidden-magic.sch, led.sch]
2014-12-23 note added on the led forward current
    [hidden-magic-cbldrv.sch, hidden-magic.sch, transimpedance.sch]
2014-12-24 changes to page numbers and connector pinouts
    [cabledrive.sch, hidden-magic-cbldrv.sch, hidden-magic.sch, led.sch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]
2014-12-26 removed current source filter, added notes on current source power
    [led.sch, transimpedance.sch]
2014-12-26 changed connectors on cable driver board to 2 pin mini molex
    [cabledrive.sch]
2014-12-26 added footprints for mini molex 4, 5, & 6 pin vertical connectors
2014-12-30 I added a lot of comments on how the transimpedance amplifier should be laidout
    [transimpedance.sch]
2014-12-30 Transimpedance amplifier footprint set
    [transimpedance.sch]
2014-12-30 set cable driver connector footprint
    [cabledrive.sch, led.sch]
2014-12-30 changed text alignment and removed a capacitor on the LED current source
    [led.sch]
2014-12-30 starting a pcb layout for the transimpedance amplifier
    [transimpedance.sch]
2014-12-30 added comments about selecting current source filter resistors.
    [led.sch]
2014-12-31 trying to make a layout, added more netnames
    [led.sch]
2014-12-31 fixed some footprint sizes on passives. starting again to do layout.
    [cabledrive.sch, led.sch, transimpedance.sch]
2015-03-23 finished backpanel in 2 board layout only to realize it made more sense as 3
    [cabledrive.sch, cover.sch, hidden-magic-cbldrv.sch, led.sch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]
2015-03-23 finished the cover more or less moving on to the revised output driver
    [cabledrive.sch, cover-art.bottom.gbr, cover-art.bottommask.gbr, cover-art.bottomsilk.gbr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]
2015-03-24 changed photodiode polarity, make new board just for output amps, etc
    [cabledrive.sch, cover-art.bottom.gbr, cover-art.bottommask.gbr, cover-art.bottomsilk.gbr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]
2015-03-25 fixed the page numbering and some part values and numbers
    [cabledrive.sch, cover-art.bottom.gbr, cover-art.bottommask.gbr, cover-art.bottomsilk.gbr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]
2015-03-25 fixed the solder mask on the revised transimpedance amplifier
    [opticamp-art.bottom.gbr, opticamp-art.bottommask.gbr, opticamp-art.bottompaste.gbr, opticamp-art.bottomsilk.gbr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]
2015-04-10 more work on the front panel
    [cover-art.bottom.gbr, cover-art.bottommask.gbr, cover-art.bottomsilk.gbr, cover-art.fab.gbr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]
2015-04-16 cleanup of spurious footprints
    [opticamp-art.bottom.gbr, opticamp-art.bottommask.gbr, opticamp-art.bottompaste.gbr, opticamp-art.bottomsilk.gbr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]
2015-05-05 fixed D1 and LED1 footprint issues (pin spacing) and D1 & LED1 alignment relative to outline
    [cover-art.gbl, cover-art.gbo, cover-art.gbs, cover-art.gko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]
2015-05-08 finished version 2.1
    [opticamp-art.bottom.gbr, opticamp-art.bottommask.gbr, opticamp-art.bottompaste.gbr, opticamp-art.bottomsilk.gbr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]
2015-05-08 changing over to using LTC6268 for TIA
    [transimpedance.sch]
2017-07-19 moved to LT1793
    [cabledrive-annotated.sch, cabledrive.sch, cover-art.bottom.gbr, cover-art.bottommask.gbr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]
2025-03-17 add: images of the pcb layouts
2025-03-18 add: pictures of the completed device
2025-03-18 fix: reverse bias had a backwards capacitor
2025-03-18 add: images of the completed PCBA now included in readme
2025-03-18 add: revised images for assembled pcba
2025-03-22 del: removed old gerbers
    [cover-art.bottom.gbr, cover-art.bottommask.gbr, cover-art.bottomsilk.gbr, cover-art.fab.gbr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]
2025-03-22 del: more spurious gerbers removed
    [opticamp-art.bottom.gbr, opticamp-art.bottommask.gbr, opticamp-art.bottompaste.gbr, opticamp-art.bottomsilk.gbr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]
